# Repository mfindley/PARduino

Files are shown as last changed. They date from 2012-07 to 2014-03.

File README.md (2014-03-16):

PARduino
========

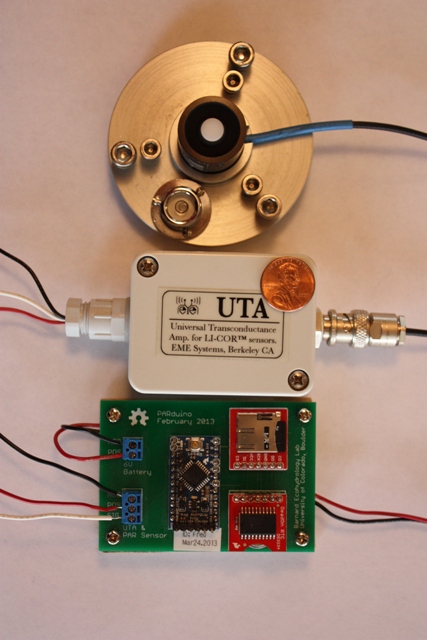
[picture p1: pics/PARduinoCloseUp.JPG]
PARduino Image of PARduino Hardware


PARduino measures and logs photosynthetically active radiation (PAR). 
It was designed for the Barnard Ecohydology Lab at the University of Colorado, Boulder  (http://instaar.colorado.edu/research/labs-groups/ecohydrology-laboratory/).

Introduction
------------
PAR is measured during environmental monitoring and research.  We developed PARduino because it has the potential to collect environmental data in research plots at a lower cost than what we currently use for data aquisition.

Design Files
------------
PARduino is shared with the community as open source hardware (OSHW).  We hope others find it useful and will extend, modify, and otherwise improve the design.  With that in mind, this GitHub repository contains design files associated with the PARduino:
 - The Arduino code used to poll the sensor and store the measurement on a microSD flash card.
 - Designs for a printed circuit board connecting all the components.
 - A bill of materials listing parts and tools required to create a PARduino.

Making PARduino
---------------
- Procure components using the bill of materials.
- Wire the components together on a breadboard or mount them on the PCB.
- Modify the software for the gainfactor of the EME amplifier and the calibration factor of the Li-COR sensor (each Li-COR sensor has a different calibration factor).  This entails changing these values at the beginning of the PARduino source code.
- Set the time and date on the real time clock.
- Format the microSD flash card.
- Load the software onto the microcontroller using FDTI USB-to-Serial breakout board.

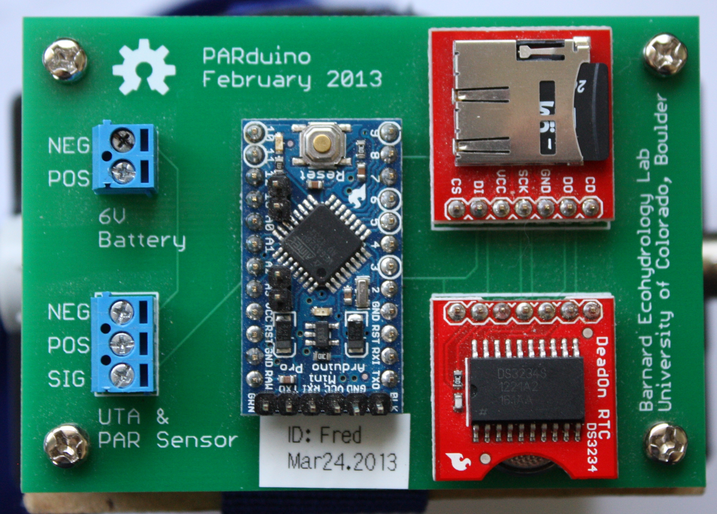
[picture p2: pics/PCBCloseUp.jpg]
Close up of the PCB with components
 

Using PARduino
--------------

There's really no on/off switch at this stage of development.  The device starts up as soon as it is powered.  Hitting the reset button on the Arduino Pro Mini will restart the firmware and append another block of initiallization text to the data file.  Harmless, but results in a cluttered data file.

Design Rationale
----------------

We selected the electronic components with an eye towards ease of assembly - everything can be soldered to the PCB using through-hole soldering techniques.  Since the device will be deployed in remote research plots that lack easy access to line power, battery life was also a consideration in the design.  This drove the decision to use the 3.3 Volt and 8 megahertz version of Sparkfun's Arduino Pro Mini.  This Arduino board uses less power than an Arduino Uno (both because of voltage and because it lacks the onboard USB to serial converter of the Uno).  It also drove the design of the microcontroller software - remaining in low power sleep mode until the device is ready to make a measurement dramatically extends field deployment times.

We use a 6 volt sealed lead acid battery because is has the amp-hours (listed as 8.2Ah) for extended field deployment, because it has a voltage that is high enough to run the EME amplifier (not to mention availability - there was a BatteriesPlus in town), and because the battery, while large by standards for cell phones and other consumer electronic devices, is still much  smaller than the 12 V sealed lead acid marine batteries that are commonly deployed at remote research plots.

License
-------
The code and other design documents for PARduino are released under the Creative Commons Attribution-ShareAlike 3.0 United States License. To view a copy of this license, visit http://creativecommons.org/licenses/by-sa/3.0/us/ or send a letter to Creative Commons, 444 Castro Street, Suite 900, Mountain View, California, 94041, USA.

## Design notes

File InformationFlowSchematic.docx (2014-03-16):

EME Systems’
UTA

PAR Value with Time/Date Stamp

microSD
Memory Card

Wake Signal and Time/Date Every Minute

Real Time Clock

SparkFun
Arduino Pro Mini

LiCor LI-190 Quantum PAR Sensor

PAR
Sensor

Amplifier

Micro-
controller

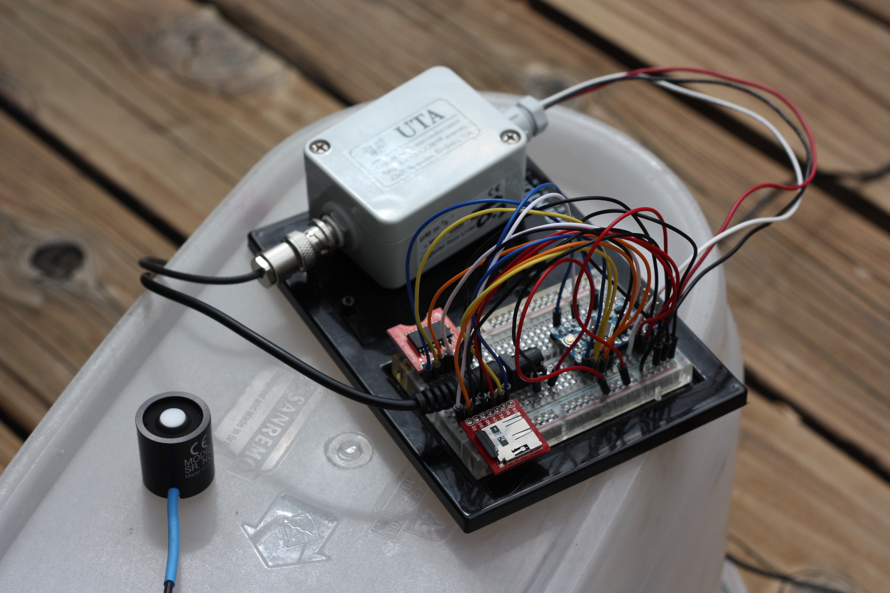
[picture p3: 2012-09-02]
pics/PrototypePARduino.JPG

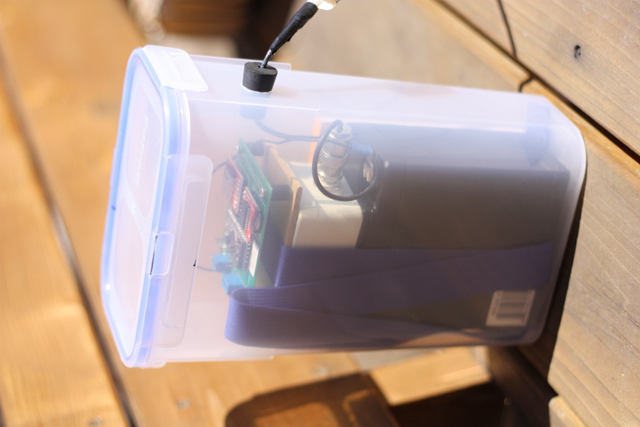
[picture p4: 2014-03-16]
pics/EnclosureCloseUp.JPG

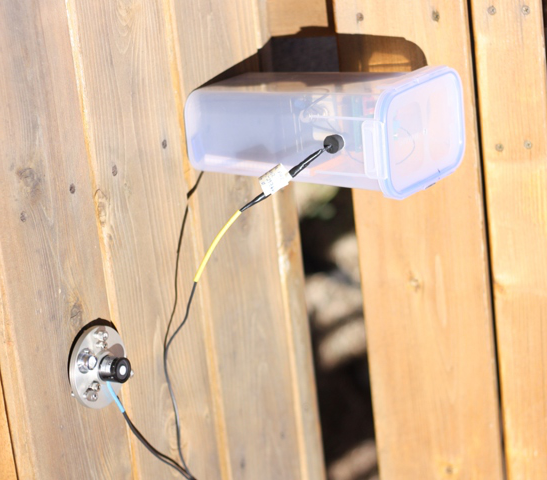
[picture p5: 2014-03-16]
pics/EnclosureAndSensor.JPG

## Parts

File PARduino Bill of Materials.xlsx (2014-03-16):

Item | Description | Unit Price | Quantity | Unit | Part Number | Hyperlink
1 | Arduino Pro Mini 3.3V/8MHz | $18.95 | 1 | ea | Sparkfun DEV-11114 | https://www.sparkfun.com/products/11114
2 | microFlash SD Socket breakout board | $9.95 | 1 | ea | BOB-00544 | https://www.sparkfun.com/products/544?
3 | DeadOn real time clock breakout board | $19.95 | 1 | ea | BOB-10160 | https://www.sparkfun.com/products/10160
4 | PAR Sensor | $500.00 | 1 | ea | LI-190SA | http://www.licor.com/env/products/light/quantum_sensors/190specs.html
5 | PAR Amplifier | $150.00 | 1 | ea | UTA/BNC/190/gain=/NE | http://www.emesystems.com/uta_dat.htm | NE = no enclosure
6 | 6V Battery | $25.00 | 1 | ea | Werker WKA6-8.2F | http://www.batteriesplus.com/product/32653-WKA6--8-dot2F-Werker-6V-8-dot2Ah-Battery/100085-1/102629-SLA-Sealed-Lead-Acid-Batteries/102647-Werker/6V.aspx
7 | Printed Wiring Board | $13.30 | 1 | ea
8 | 2 pin Screw Terminal | $0.95 | 1 | ea | PRT-08084 | https://www.sparkfun.com/products/8084
9 | 3 pin Screw Terminal | $0.95 | 1 | ea | PRT-08235 | https://www.sparkfun.com/products/8235
10 | breakaway headers | $2.95 |  |  |  | https://www.sparkfun.com/products/117
11 | 0.187" faston battery connector | $2.00 | 2
12 | standoffs and screws | $5.00 |  |  | approx
13 | 40 inch strap with buckle | $7.00 | 1 |  |  | http://www.rei.com/product/848429/redpoint-34-webbing-straps-with-side-release-buckles-package-of-2
14 | enclosure (picked up at Bed Bath and Beyond) | 7.99 | 1 | ea | 10 cup Snapware Airtight | http://www.shopworldkitchen.com/snapware/rectangle-airtight-foodstorage-container-1098431
 | tools
 | FTDI Basic to load program onto the microcontroller | 14.95 | 1
 | microSD to SD Memory Card Adapter | 3.49 | 1 |  |  | http://www.amazon.com/SanDisk-microSD-Memory-Card-Adapter/dp/B0047WZOOO/ref=pd_bxgy_pc_text_z
 | Soldering Iron
 | Solder
 | 22AWG Hook Up Wire. various colors | 16.95 |  |  |  | https://www.sparkfun.com/products/11367
 | Wire strippers
 | Wire snips

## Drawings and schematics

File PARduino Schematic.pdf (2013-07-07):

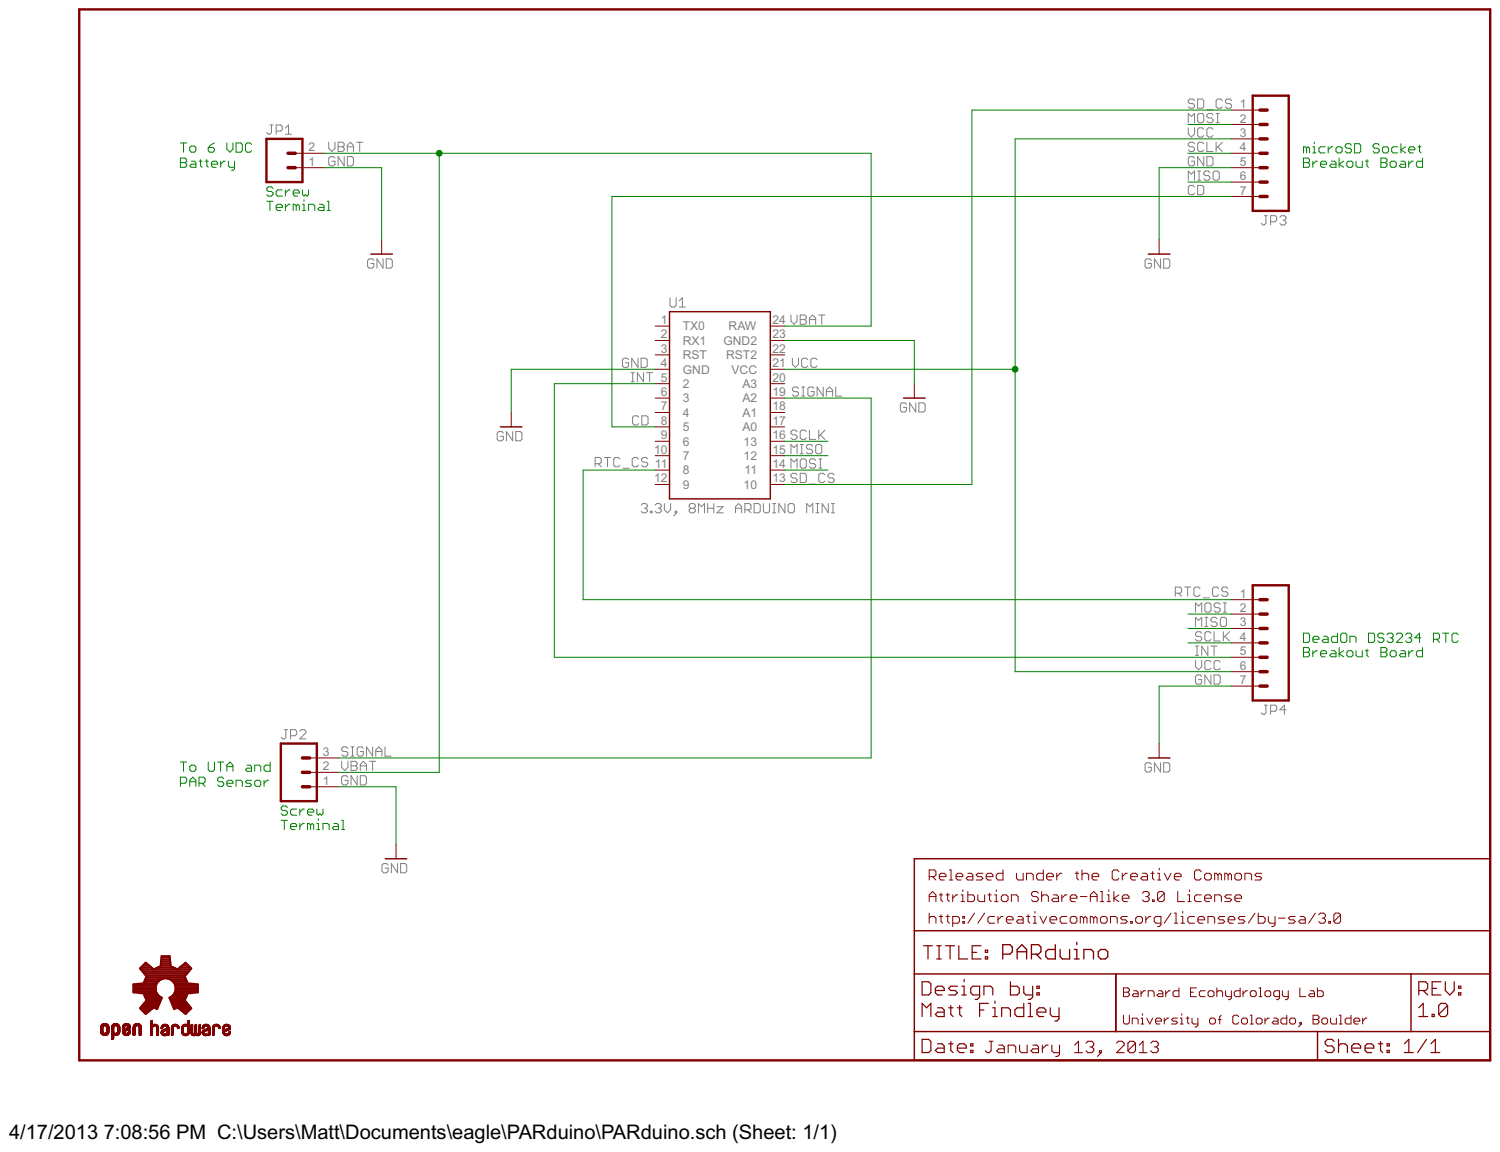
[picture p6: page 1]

4/17/2013 7:08:56 PM C:\Users\Matt\Documents\eagle\PARduino\PARduino.sch (Sheet: 1/1)

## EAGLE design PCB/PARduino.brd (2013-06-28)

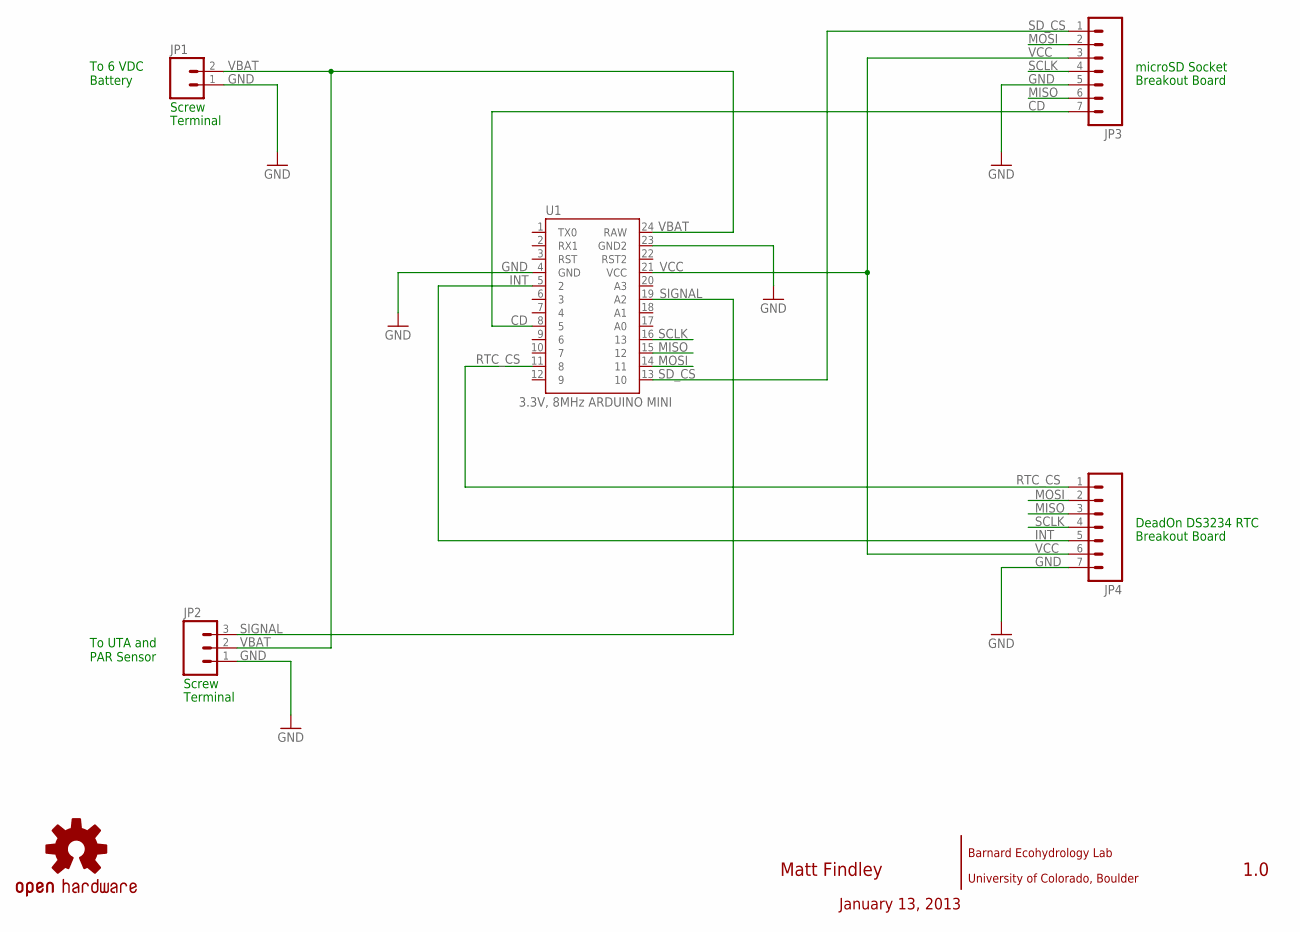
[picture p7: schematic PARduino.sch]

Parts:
JP1: M023.5MM_LOCK; SCREWTERMINAL-3.5MM-2_LOCK
JP2: M03SCREW; SCREWTERMINAL-3.5MM-3
JP3, JP4: M07LOCK; 1X07_LOCK
LOGO: OSHW-LOGOL; OSHW-LOGO-L
U1: 3.3V, 8MHz ARDUINO MINI; ARDUINO_MINI

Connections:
CD: JP3.7, U1.8 (5)
GND: JP1.1, JP2.1, JP3.5, JP4.7, U1.4 (GND), U1.23 (GND2)
INT: JP4.5, U1.5 (2)
MISO: JP3.6, JP4.3, U1.15 (12)
MOSI: JP3.2, JP4.2, U1.14 (11)
RTC_CS: JP4.1, U1.11 (8)
SCLK: JP3.4, JP4.4, U1.16 (13)
SD_CS: JP3.1, U1.13 (10)
SIGNAL: JP2.3, U1.19 (A2)
VBAT: JP1.2, JP2.2, U1.24 (RAW)
VCC: JP3.3, JP4.6, U1.21 (VCC)

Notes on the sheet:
To UTA and PAR Sensor
To 6 VDC Battery
Screw
Terminal
microSD Socket
Breakout Board
DeadOn DS3234 RTC
Matt Findley
Barnard Ecohydrology Lab
University of Colorado, Boulder
January 13, 2013
1.0

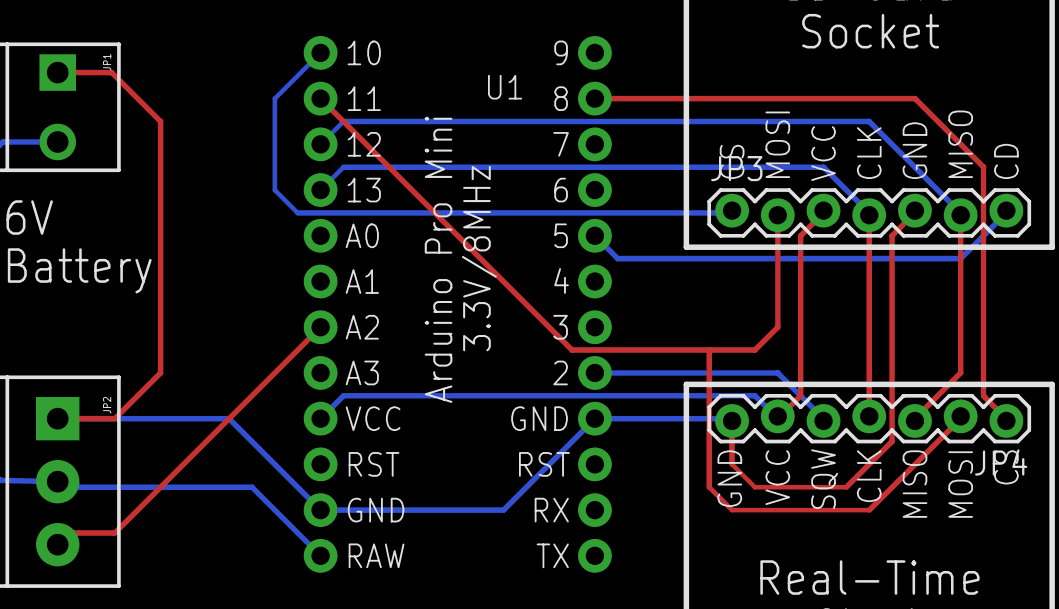
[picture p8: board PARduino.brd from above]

Board: 2 copper layers, 10 parts (0 on the bottom side), 11 nets.

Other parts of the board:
U$1, U$2, U$3, U$4: STAND-OFF

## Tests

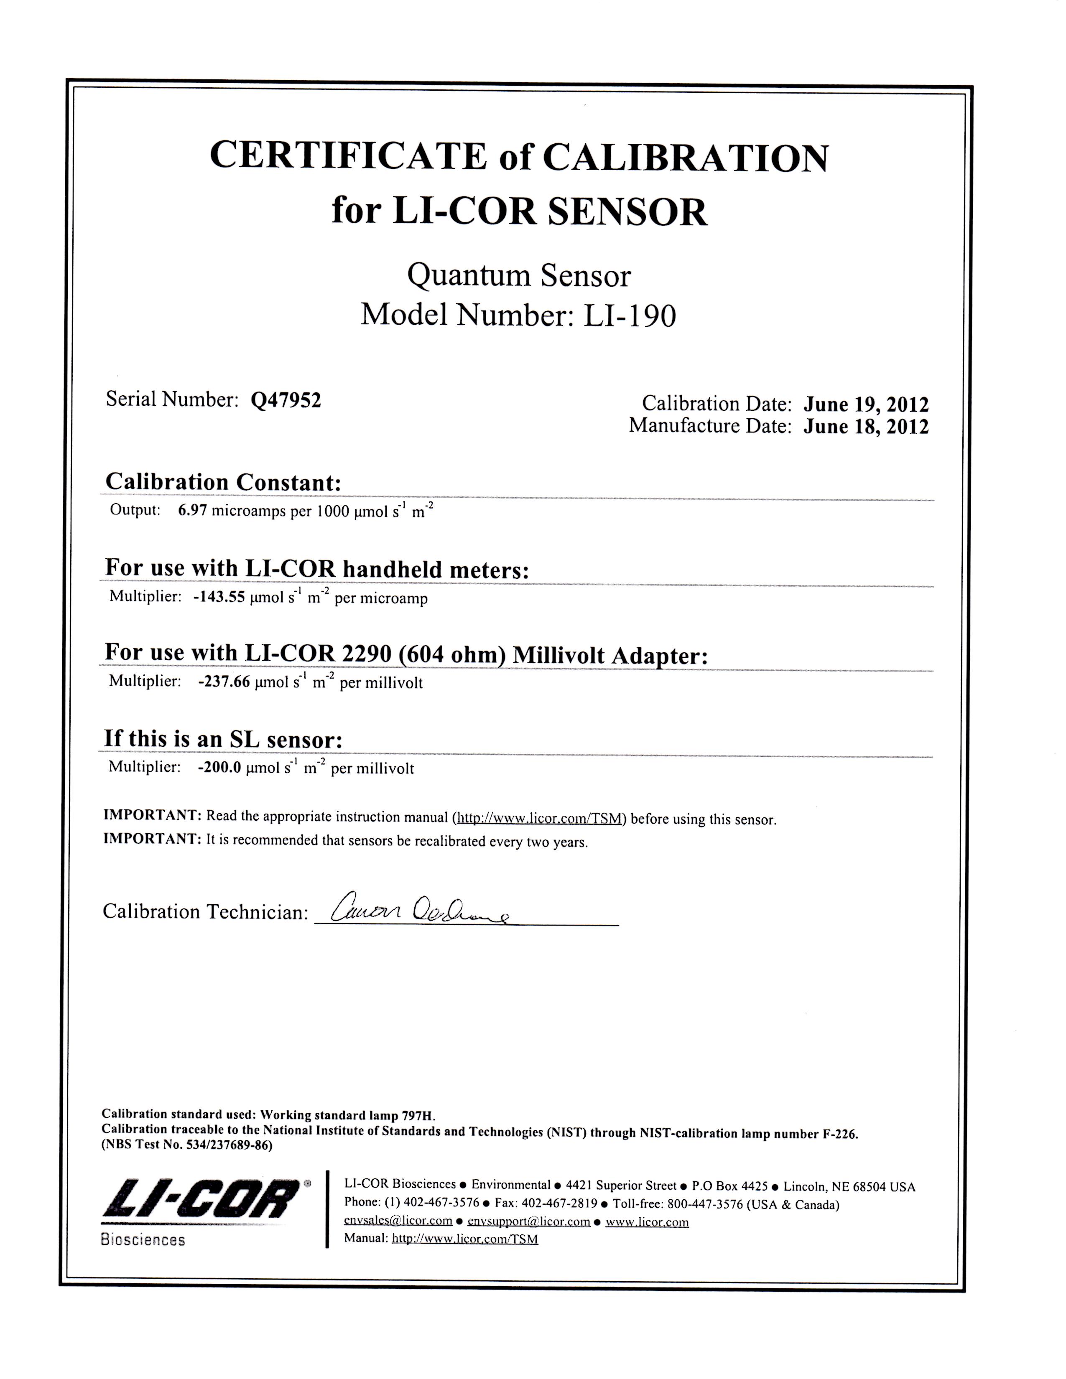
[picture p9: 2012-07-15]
LiCOR calibration page.jpg

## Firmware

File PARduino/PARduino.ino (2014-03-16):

/*3456789112345678921234567893123456789412345678951234567895123456789612345678971234567898

PARduino measures and logs photosynthetically active radiation (PAR). 

This is a adobe acrobat portable document format (pdf) listing of the source code.  See:
  https://github.com/mfindley/PARduino
for source code that can be imported into the Arduino IDE.

It was designed for the Barnard Ecohydology Lab at the University of Colorado, Boulder
 http://instaar.colorado.edu/research/labs-groups/ecohydrology-laboratory/ .

The program is designed for the following components:
 - an Arduino Pro Mini (8 mHz / 3.3 volts built around the ATmega328)
   https://www.sparkfun.com/products/11114?
 - DeadOn Real Time Clock - DS3234 Breakout Board
   https://www.sparkfun.com/products/10160
 - microSD card breakout board https://www.sparkfun.com/products/544?
 - EME Systems Universal Transconductance Amplifier (UTA) w/ BNC connector 
   http://www.emesystems.com/uta_dat.htm 
   http://www.emesystems.com/pdfs/UTA_ver2A_120407.pdf 
 - LI-COR Quantum PAR sensor(Li-190SA version with a BNC connector)
   http://www.licor.com/env/pdf/light/190.pdf

Created using version 1.0.5 of the Arduino IDE.

Program notes:

  The microcontroller sleeps in low power mode when not acquiring data.  
  This is based loosely on the example at:
    http://www.engblaze.com/hush-little-microprocessor-avr-and-arduino-sleep-mode-basics/
  but modified to wake on an external interrupt triggered when the RTC alarms on the 
  minute at 00 seconds.

  Configuring and formatting the clock data is based on the Sparkfun example at: 
  http://dlnmh9ip6v2uc.cloudfront.net/datasheets/BreakoutBoards/DS3234_Example_Code.pde
  but modified to set the alarm, set the interrupt, and to read time/date using a 
  multi-byte read on the DS3234 real time clock.
  
   ... wanted to read clock using multi-byte read because page 11 of the data sheet, 
     http://www.sparkfun.com/datasheets/BreakoutBoards/DS3234.pdf , 
   suggests that this keeps registers from updating during a read cycle. 

  Initalizing of the SD card and writing to the file is based on an example, 
  ReadWriteSdFat, at  http://code.google.com/p/sdfatlib/ .
  
  Program uses example code from  http://www.arduino.cc/en/Tutorial/InputPullupSerial to 
  use the card detect pin on the SD card breakout board to detect the presense/absense 
  of an SD flash memory card in the socket. 

Dependencies: 
  Except for the SdFat library,  all of the other software libaries used by this code are
  included in the Arduino 1.0.5 IDE.
  
  This program uses the 2013 06 29 SdFat library at http://code.google.com/p/sdfatlib/

Signal Conversion Notes:

 Program is designed specifically for a new LI-COR Quantum sensor purchased by the 
 Barnard Ecohydrology Lab.  Serial number "Q 47952".  The cert. of calibration 
 (Jun 19, 2012) has a calibration constant of 6.97 microamps per 1000 umol s^-1 m^-2.
 This equates to 143.47 umol s^-1 m^-2 / microamp.
 The UTA was configured to have a "gain factor" of 0.2 V / uA when the signal is amplified
 and converted from current to voltage.

 The EME data sheet says that, to convert the signal to PAR level, 
 you need to use the formula:
   
 PAR [umol s^-1 m^-2]  = UTA Output [V]  *  LICOR Cal Multiplier [umol s^-1 m^-2 / uA]
                         -------------------------------------------------------------
                                            UTA gain factor [V / uA]

 ... the units cancel out, so what could go wrong?
 
 The LI-COR sensor and the UTA are connected to the Arduino with three wires:
   a power line, a ground line, and a signal line.  
 The signal wire feeds into pin A0. The supply voltage to the UTA must be at least 5 volts
 and must be 1 volt greater than the full scale output of the amplifier.
 
Circuit Notes:  
  pin map:
  RAW o-----o 6V sealed lead acid battery, red wire for UTA power.
  GND o-----o 6V sealed lead acid battery, black ground wire for UTA power, 
              GND wires for RTC and SD card.
  VCC o-----o VCC to SD card and the RTC.
  
  A2  o-----o white signal wire from the UTA.
  D2  o-----o interrupt (INT) pin on RTC break out board (BoB).
  D5  o-----o card detect (CD) on SD BoB.
  D8  o-----o chip select (CS) on RTC.  used for SPI communication.
  D10 o-----o chip select (CS) for the SD card.  used for SPI communication.
  D11 o-----o master out slave in (MOSI) line for the RTC and the SD card.  used for SPI.
  D12 o-----o master in slave out (MISO) line for the RTC and the SD card.  used for SPI.
  D13 o-----o clock for SPI communication. connected to CLK on the RTC and the SD card.

  Design documents for a printed circuit board (PCB) connecting all these components are 
  available at the PARduino github repository.

License:

  This work is licensed under the Creative Commons Attribution-ShareAlike 3.0 United 
  States License. To view a copy of this license, visit: 
    http://creativecommons.org/licenses/by-sa/3.0/us/ 
  or send a letter to Creative Commons, 444 Castro Street, Suite 900, Mountain View, 
  California, 94041, USA.

  Created by Matt Findley, Boulder, Colorado, Sep 1, 2012.  matthewfindley@hotmail.com.

Change log:  
9/1/2012   - added annotation.
6/28/2013  - point license for arduino code to Creative Commons Attribution-ShareAlike.
           - documented library dependencies.
           - provided reference to PCB in the PARduino GitHub repository.
7/20/2013  - provided more text info written in the header of the data file during
             initialization.
           - now includes PAR sensor serial number, calibration and gain factors
             (hard coded in)
           - time zone (hard coded as mountain standard time, but the code has no way to
             check this.)
10/22/2013 - Migrated to 1.0.5 IDE.  Added logic to take advantage of the card detect pin 
             on the flash card socket.
3/15/2014  - Reformatted to 80 char column width.
*/

// libraries used to shuffle data between MCU and the clock and memory card peripherals.
#include <SdFat.h>  // downloaded sdfatlib20130629.zip file from google code page.
#include <SPI.h>    // serial peripheral interface.
// these libraries are used to move in and out of low power mode:
#include <avr/interrupt.h>  
#include <avr/power.h>
#include <avr/sleep.h>
#include <avr/io.h>

const int cardDetectPin = 5;
const int RTC_CS=8; //chip select pin for real time clock
const int SD_CS=10; //chip select pin for SD card
const int UTA_PIN=A2; // reads the LiCOR through the UTA using analog pin 2

const int RTC_INTERRUPT=0;   // catching the RTC alarm using Interrupt0 on the MCU.                           
                             // Interrupt0 maps to pin D2 on the Arduino and is variously 
                             // identifed by pin number or by interrupt number, which is a 
                             // bit confusing.

volatile int interruptFlag = 0;    // declare a variable to act as an interrupt flag.  
                                   // set up as volatile variable because we work with it 
                                   // in the interrupt service routine.

// constants for converting the raw signal to a PAR value
const float REFERENCE_VOLTS = 3.3; // create variable (floating number) for the max 
                                   // voltage on the Arduino's analog-to-digital (ADC) 
                                   // converter.

// see intro to program for explanation for the following "magic numbers":
const float LICOR_CAL_MULTIPLIER = 143.47;
const float UTA_GAIN_FACTOR = 0.20;

// variables for sampling data: 
float measuredPAR;             // create variable (floating number) that holds the PAR
                               // measurement.
String measurementTimeDate;    // string to hold the date and time for the measurement.
int cardPresent;               // variable to track if a memory card is in the slot.

SdFat sd;  // used by the SDFat library to create an C++ object representing the SD card
SdFile myFile;  // used by SDFat to create an C++ object representing the data file

void setup(void)
{
  //start serial connection
//  Serial.begin(9600);
  pinMode(RTC_CS, OUTPUT);  // set the chip select pin to out before anything else!!!
  pinMode(SD_CS, OUTPUT);  // set the chip select pin to out before anything else!!!
  pinMode(cardDetectPin, INPUT_PULLUP); // set pin2 as an input w/ internal pull-up
                                        // resistor

  initializeRTC();   // set alarm2 and enable interrupt on the DS3234
   // sets up interrupt0 to trigger whenever the RTC alarm falls from high to low:
  attachInterrupt(RTC_INTERRUPT, RealTimeClockInterruptServiceRoutine, FALLING); 

  cardPresent = digitalRead(cardDetectPin);
  while (cardPresent == LOW)   
  {
    // hang in this loop until the SD card is detected in the socket.
    cardPresent = digitalRead(cardDetectPin);
    delay(500);
  }
  // most of the following code is from the ReadWriteSDFat example code
  // that comes with the SDFat library.
  
  if (!sd.begin(SD_CS, SPI_HALF_SPEED)) sd.initErrorHalt();

  // open the file for write at end like the Native SD library
  if (!myFile.open("PARData.txt", O_RDWR | O_CREAT | O_AT_END)) {
    sd.errorHalt("opening PARData.txt for write failed");
  }
  // if the file opened okay, write to it:
  myFile.print("#Header Text... Initialized:  ");
  myFile.println(readTime());
  myFile.println("#PAR Sensor Model: LI190  Serial Number: Q47952");
  myFile.println("#Calibration Constant: 143.47 micromol s-1 m-2 / microamp");
  myFile.println("#Amplifier Gain: 0.2 Volt / microamp");
  myFile.println("#Time Zone:  Mountain Standard Time");
  // close the file:
  myFile.close();
}

void loop()
{
  sleepNow();
  if(interruptFlag == 1)
  {
    cardPresent = digitalRead(cardDetectPin);
    if (cardPresent == HIGH) 
    {
      measurementTimeDate = readTime();    // calls function that reads the time and date
                                           // off the real time clock.

      measuredPAR = acquirePAR();          // calls function that reads voltage on Analog 
                                           // pin 0 and converts it to PAR level.

      if (!myFile.open("PARData.txt", O_RDWR | O_CREAT | O_AT_END)) {
        sd.errorHalt("opening test.txt for write failed");
      }
      // if the file opened okay, write to it:
      myFile.print(measurementTimeDate);
      myFile.print("\t");
      myFile.println(measuredPAR);
      myFile.close();
    } 
    else 
    {
//      Serial.println("Card Not Present");
    }
  clearInterruptFlag();  // this must be done before going back to sleep
  }
}

void initializeRTC()
{
  SPI.begin();  // start command for SPI.  used in Sparkfun's example code
  SPI.setBitOrder(MSBFIRST);  // configuration command used to communicate with the clock.
  SPI.setDataMode(SPI_MODE3); 

 // configure the Alarm 2 control registers on the RTC to fire an interrupt on 00 seconds
 // of every minute - see table 2 of DS3234 datasheet.
  digitalWrite(RTC_CS, LOW);  // pull the chip select pin connected to the RTC low, so 
                              // that the RTC knows that the Arduino wants to communicate 
                              // with it.

  SPI.transfer(0x8B);         // send a command which contains the register address that 
                              // we want to write to.  
                              // 0x8B is the first register in the series of alarm2 
                              // programming registers.
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

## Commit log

2012-07-02 add sketch and notes
    add arduino sketch and random notes about the project to the repository.
2012-07-03 put sketch in folder
    Arduino IDE says that the *.ino sketch needs to be in its own folder?
    OK.
2012-07-03 separated PC and data logger serial streams
    used Arduino 1.0's SoftwareSerial library to send all the debugging info
    down the USB's serial line to the PC, but send only the final
    measurements to the OpenLog device. ... also created a "Do Nothing"
    sketch that essentially wipes the previous sketch from the
    microcontroller, so that it doesn't dump a bunch of junk to the OpenLog
    while a new sketch is being uploaded. ... not pretty, but works.
2012-07-07 more sketch files used to figure out the clock
    ... created several arduino sketches used to figure out the
    configuration of the clock, particularly the Alarm and Interrupts.
    ... also created a version of the logging sketch that captures discrete
    measurements instead of calculating and recording average values.
2012-07-15 re-organized, created sketch w/ interrupts
    Re-organized the files to put all the intermediate sketches used to
    understand Arduino Interrupts and RTC configuration in separate folders.
    Created a version of the PAR data logging sketch that uses interrupts -
    it now logs data whenever there are 00 seconds on the clock.
    [sample data.xlsx]
2012-09-02 remove all intermediate sketches except for PARduino
    ... cleaned up the GIT directory by removing all the previous sketches
    related to this project (most were small fragments designed to better
    understand the peripherals).
    Attached the GNU GPL to the sketch.
    [sample data.xlsx]
2012-09-02 add pic
    added picture of sensor and components on a breadboard.
2013-06-28 documentation updates
    changed to a creative commons license.
    documented library dependencies.
    referenced the printed circuit board.
2013-06-28 added PCB eagle files and bill of materials
    [PARduino Bill of Materials.xlsx, PARduino.GBL, PARduino.GBO, PARduino.GBS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]
2013-06-28 further tweaks to documentation.
    updated reference to the PCB now that PCB design documents have been added to the GitHub repository.
2013-12-01 card detect
    re-worked the code to take advantage of the card detect switch on the
    flash memory card and socket.
    [DATA.xlsx, PARduino Bill of Materials.xlsx]
2014-03-09 Updated PARduino.ino to run on arduino 1.0.5 IDE
    [PARduino Bill of Materials.xlsx, resolution calcs.xlsx]
2014-03-16 Added pics and folder for pics
    added several photos of the device to the project directory and put them
    in a separated pics subdirectory.

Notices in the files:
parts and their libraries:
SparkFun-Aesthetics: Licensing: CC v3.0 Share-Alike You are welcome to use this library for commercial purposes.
